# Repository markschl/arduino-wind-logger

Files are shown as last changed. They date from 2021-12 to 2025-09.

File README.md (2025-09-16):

# Data loggers for the ATMOS22 wind sensors (METER)

This repository describes the assembly and operation of low-cost data loggers for the [ATMOS 22 ultrasonic anemometer](https://www.metergroup.com/en/meter-environment/products/atmos-22-ultrasonic-anemometer) (METER group). Two different assemblies of Arduino-compatible components are presented with the programming code needed to operate the loggers in low-power mode. The output files with wind and temperature measurements are saved on a microSD card.

## Logger assembly

Two kinds of logger boards with a microSD card holder were used: [SODAQ Autonomo](https://support.sodaq.com/Boards/Autonomo) (discontinued) and [Adafruit Feather M0 Adalogger](https://learn.adafruit.com/adafruit-feather-m0-adalogger). An [external DS3231 RTC](https://learn.adafruit.com/adafruit-ds3231-precision-rtc-breakout) was connected for timekeeping and waking up the device from sleep mode. A button (switch) was connected to one of the pins and ground to interact with the logger. The pin numbers, to which RTC, button and sensor were connected are defined in `SodaqAutonomo.h` and `FeatherM0.h`.

The boards were powered by a 2700mAh Li-Ion battery, which was charged by a small 0.5 W / 100mA solar panel. The SODAQ Autonomo has an integrated solar power management circuit, while the Feather M0 Adalogger was powered by a separate [solar power manager](https://wiki.dfrobot.com/Solar_Power_Manager_5V_SKU__DFR0559) (DFROBOT DFR0559) providing a 5V power source and connected by USB, simultaneously providing power to the ATMOS22 sensor, which requires of minimum 3.6 V. For the SODAQ Autonomo wit an operating voltage of 3.3V, an additional [DC/DC boost converter](https://learn.adafruit.com/adafruit-powerboost) was needed to provide a 5V source. The solar chargers seem not to adapt to cold (< 0 °C) temperatures and thus may not be ideal for continued operation in winter.

Simple diagrams of the wiring created using the software [Fritzing](https://fritzing.org/download/) are [provided here](circuits).

## How to program the loggers

### Setup

First, install the [Arduino IDE](https://www.arduino.cc/en/software) and start it.

Next, board support has to be installed by clicking on File -> Preferences and pasting the necessary JSON file URLs (separated by comma) into the text field at "Additional Boards Manager URLs". Then go to Tools -> Boards Manager, and intall the following:

- [SODAQ Autonomo](https://support.sodaq.com/getting_started/): `http://downloads.sodaq.net/package_sodaq_samd_index.json`, provides *SODAQ SAMD Boards*
- [Adafruit Adalogger](https://learn.adafruit.com/adafruit-feather-m0-adalogger/setup): `https://adafruit.github.io/arduino-board-index/package_adafruit_index.json`, provides *Adafruit SAMD Boards*

#### Ubuntu Linux

For Ubuntu, access to the serial port has to be granted by typing this in the terminal: `sudo adduser $USER dialout`. Then log out and in again.

### Arduino libraries

A few libraries are needed (Tools -> Library Manager):

- *SdFat* by Bill Greimann (tested with versions 2.3.0)
- *RTClib* by Adafruit (2.1.4)
- *Arduino Low Power* by Arduino LLC (1.2.2)
- [*SDI-12*](https://github.com/EnviroDIY/Arduino-SDI-12) by Kevin Smith et al. (2.3.0)

### Preparation

- Open `datalogger/datalogger.ino` in the Arduino IDE. Select the correct board at *Tools -> Boards -> \<board name\>*. There are separate header files named after the boards, which include all the pin settings. If you have a different board or pin wiring, you need to adjust the code and add your own header file with the correct settings.
- **Configuration:** Adjust the variables in "User settings" section if necessary
- At a minimum, give your sensor/logger combo an unique name by setting the **LOGGER_ID**. This name is prepended to all output files and helps to avoid confusion when copying them all to your computer
- Make sure that `DEBUG` is `false` if uploading the final program for autonomous operation (the default is `DEBUG true`, which is useful for setting things up)

#### Configuration

The logger is configured to do *instantaneous measurements every 10 seconds* using the `R4!` command (see [Integrator Guide](http://publications.metergroup.com/Integrator%20Guide/18195%20ATMOS%2022%20Integrator%20Guide.pdf)). The measurement interval can easily be changed in the *User Settings* section. Switching to averaged / maximum values (`R3!` command) requires replacing `sensor.measureR4(logLine)` with `sensor.measureR3(logLine)` in `datalogger.ino`. Other commands will have to be implemented first (in `Sensor.h` / `Sensor.cpp`).

### Uploading the program to the logger

Connect the logger board to the computer using a mini-USB cable. For the the boards to be ready under Ubuntu 20.04, it was usually reqired to double tap the reset button. Make sure that the device is present under *Tools -> Port*, otherwise double tap the reset button another time. `Ctrl + U` will upload the program.

If `DEBUG` is set to `true` (the default) before the upload, the progress of the logger operation can be monitored in the serial console (Tools -> Serial Monitor) while still connected by the USB cable. This mode also allows setting the time of the RTC and formatting the SD card if necessary. For regular operation, the program should again be uploaded with DEBUG disabled.

## Preparing the SD cards

We used SD cards with 2 GB capacity (which is more than enough for long logging). Smaller cards tend to have less powerful chips that [also draw less power](https://thecavepearlproject.org/2015/11/05/a-diy-arduino-data-logger-build-instructions-part-4-power-optimization). Cards smaller than 2GB should be formatted to FAT16. In Linux, this can be done as follows (given the device of the SD card):

```sh
sudo mkdosfs -F 16 /dev/sdb1
```

Alternatively, the logger is able to detect problematic formatting and format the SD card when in debug mode (see above).

## Logger operation

Make sure to upload the program with `DEBUG` set to `false`.

- Startup is indicated by the LED blinking 10x. The SD card must be present. The LED will also light up during wind measurement (which takes a bit less than a second).

- Errors are indicated by the LED blinking 3-5 times every 10 seconds. 3x indicates an error with the SD card (not inserted, wrong format or any writing error). 4x indicates an error with the sensor (not connected, ...). 5x indicates a problem with the clock (RTC). To restart the logger, press the control button or board reset button.

- Before removing the SD card, press the control button (not the reset button) once and wait until the LED light has disappeared. The logger will continue measuring, but blinking twice (long-short) to indicate "detached" logging. After re-inserting the SD card (or a new one), again press the control button. Further regular measurements will be indicated by the "normal" single blinking event of the LED. If the long-short blinking pattern persists, this means that the logger is still in detached mode because there was a problem with the SD card (not inserted / wrong format).

- Every time the SD card is (re-)inserted, the logger creates a new file in the `atmos22` directory named according to the insertion date. The `txt` files can later be combined in Excel or R.

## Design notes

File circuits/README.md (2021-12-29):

# Wiring diagrams

## SODAQ Autonomo

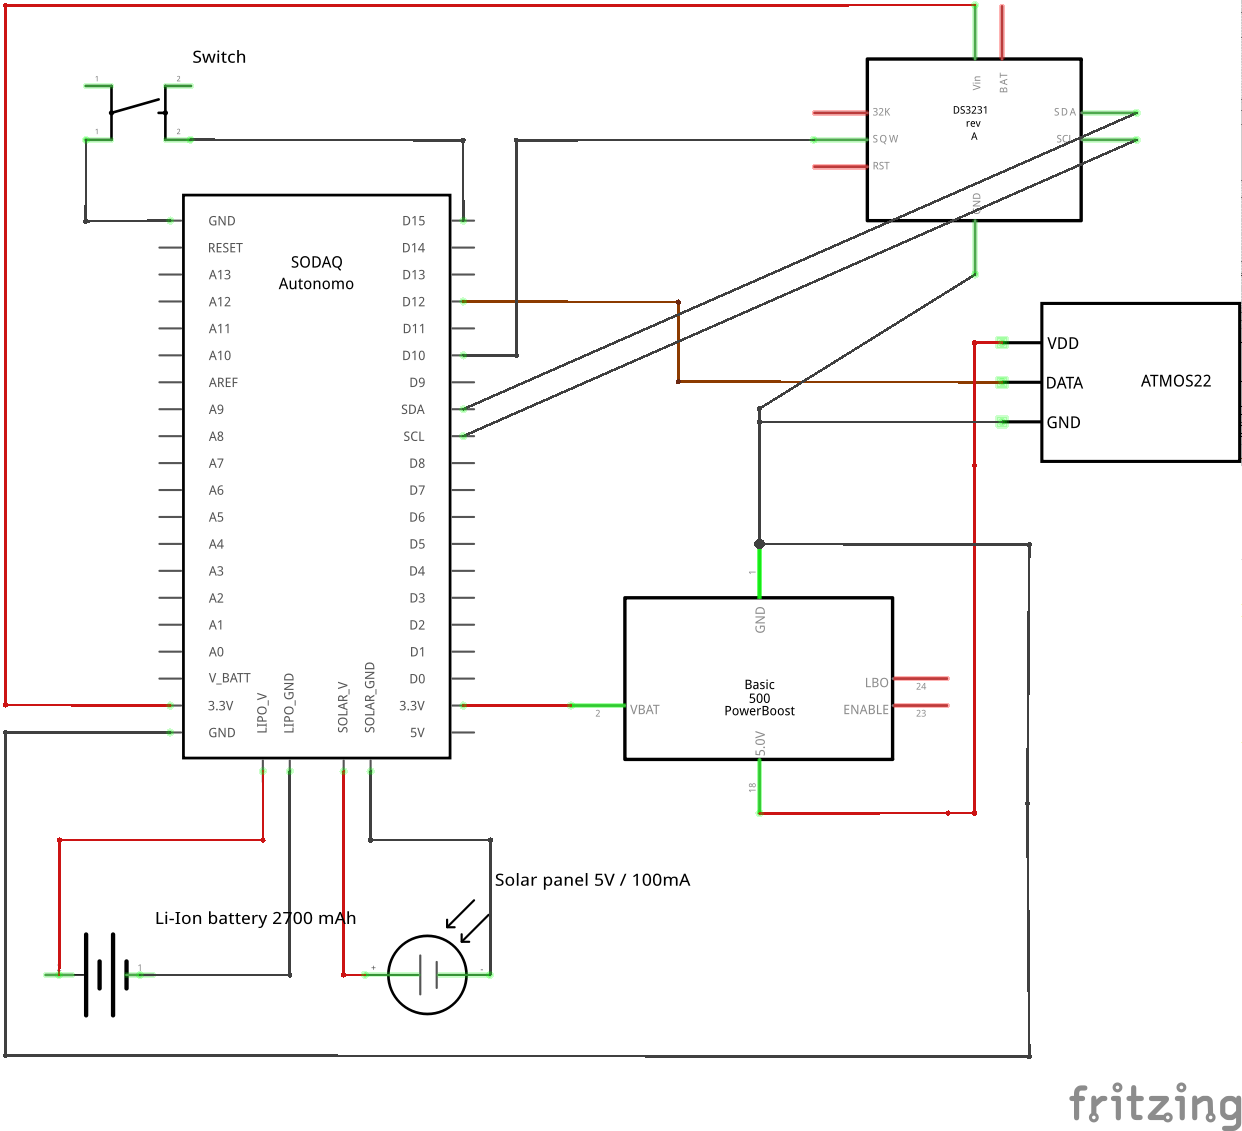
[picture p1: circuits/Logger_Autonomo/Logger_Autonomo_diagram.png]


## Adafruit Feather M0 Adalogger

The diagram does not include the [solar power manager](https://wiki.dfrobot.com/Solar_Power_Manager_5V_SKU__DFR0559) (DFROBOT DFR0559) providing the 5V USB power source.

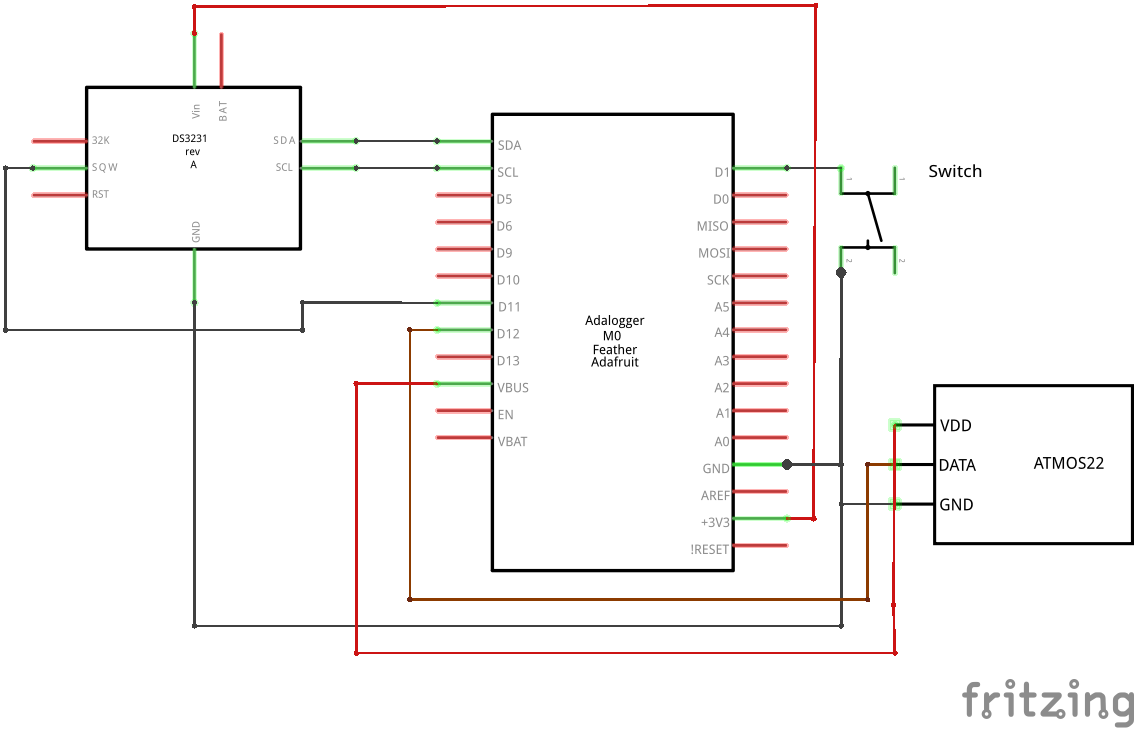
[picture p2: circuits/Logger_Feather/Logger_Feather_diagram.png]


## Fritzing files

The Fritzing parts for the solar panel and SODAQ Autonomo were [obtained here](https://github.com/GabrielNotman/SODAQ_Fritzing) and further modified. The Adafruit parts were [obtained from this page](https://github.com/adafruit/Fritzing-Library). The Li-Ion battery was modified from a battery part from the Fritzing core library. License: CC BY-SA 3.0.

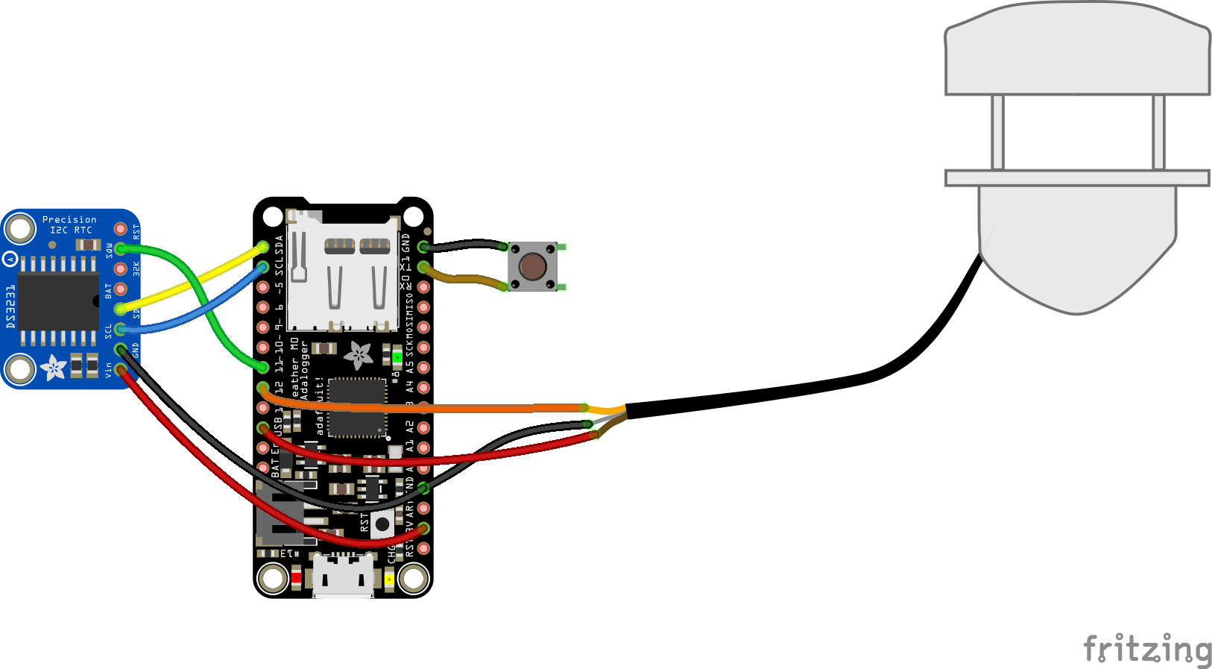
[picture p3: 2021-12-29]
circuits/Logger_Feather/Logger_Feather.png

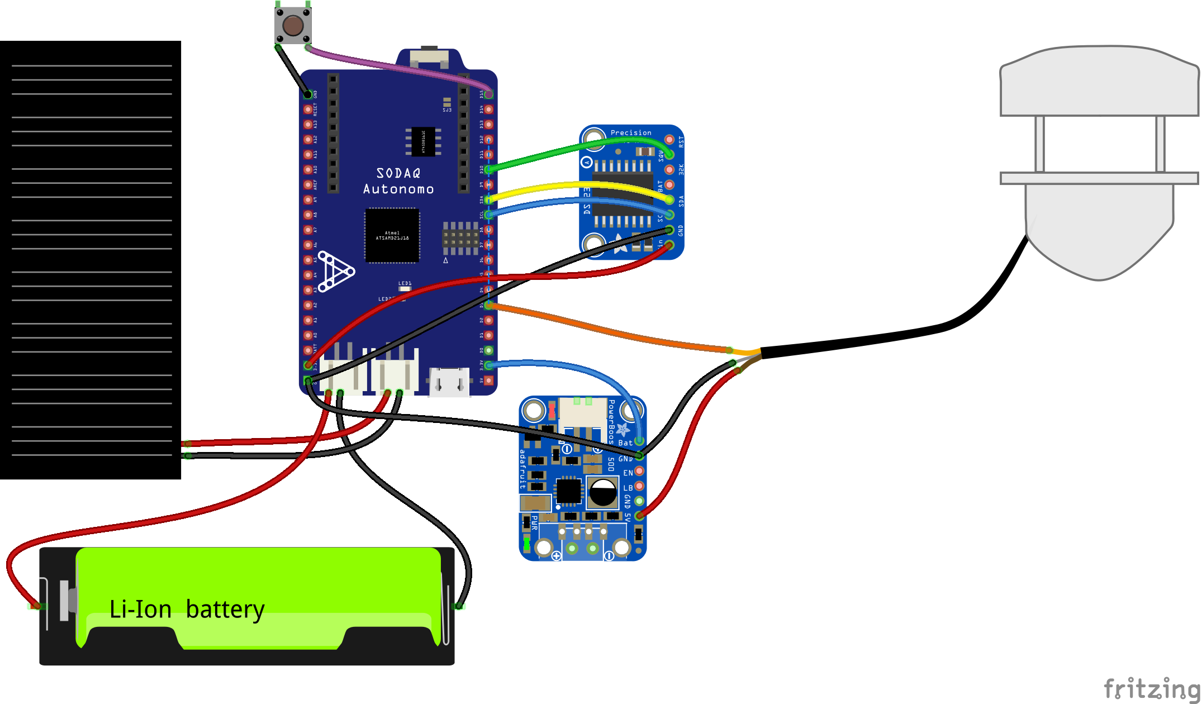
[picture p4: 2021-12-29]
circuits/Logger_Autonomo/Logger_Autonomo.png

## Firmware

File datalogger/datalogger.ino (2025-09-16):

// include libraries
#include "Arduino.h"
#include "RTClib.h"
#include "SDI12.h"
#include "SdFat.h"

// Different boards have different names for the USB serial
#define Serial SERIAL_PORT_MONITOR

// include our own header files
#include "SdLogger.h"
#include "Sensor.h"
#include "system.h"

// --------------------------------------------
// 1. Choose the right board
// --------------------------------------------
// You need to install board support:
// - Sodaq Autonomo: https://support.sodaq.com/getting_started/
// - Adafruit Feather M0: https://learn.adafruit.com/adafruit-feather-m0-adalogger/setup
// Then choose the board that you connected with USB
// - Tools -> Board -> Sodaq Autonomo
// OR
// - Tools -> Board -> Adafruit Feather M0
// Further settings (pin numbers, etc.) are found in header files named after the board,
// which are automatically included (see below)

// --------------------------------------------
// 2. User settings
// --------------------------------------------

// Name of the logger, will be prepended to output file names on the SD card
// NOTE: it is adivable to give your sensor (with its attached logger) an unique
//   name to avoid confusion after copying the files to your computer!!!
#define LOGGER_ID "sensor_1"

// Debug mode: activate with true or 1, deactivate with false or 0
// Used for:
// - debugging (device activity logged to the serial console)
// - adjusting the RTC date and time
// - formatting the SD card with FAT16
// NOTE: the logger will only work autonomously (not attached to computer)
//    setting DEBUG to false
#define DEBUG true

// Name of the output directory
#define BASE_DIR "atmos22"

// Defines how many bytes should be logged to RAM before
// writing to the SD card. Higher numbers will lead to lower
// energy consumption (less frequent writes to SD card),
// but in case of power loss, more data will be lost. 
// Also make sure that there is enough RAM. Memory is reported
// in debug mode.
#define BUFFER_SIZE 16384

// Measurement interval, at least 10s if using the R4! command
// according to ATMOS22 integrator guide
#define MEASUREMENT_INTERVAL_SECONDS 10

// header added on top of every file
#define HEADER \
"date_time\tnorth_speed\teast_speed\tgust_speed\ttemperature\t\
x_orientation\ty_orientation\tbattery_voltage\tboard_temperature\n"

// Error codes (error LED will blink this many times)
#define SD_ERROR 3
#define SENSOR_ERROR 4
#define CLOCK_ERROR 5
// interval, at which erros are indicated
#define ERROR_INTERVAL_SECS 10

// SD settings
#define ENABLE_DEDICATED_SPI 1
#define SDFAT_FILE_TYPE 1

// The baud rate for the output serial port
#define SERIAL_BAUD 9600

// --------------------------------------------
// 3. Set up board and debugging
// --------------------------------------------

#if defined(ARDUINO_SODAQ_AUTONOMO)
  #include "SodaqAutonomo.h"
#elif defined(ADAFRUIT_FEATHER_M0)
  #include "FeatherM0.h"  
#else
  #error Unsupported board
#endif

#ifndef LOGGER_ID
#error "LOGGER_ID not defined"
#endif

// debugging macros
#if DEBUG

bool debugMode = true;
#define PRINT(...) Serial.print(__VA_ARGS__)
#define PRINTLN(...) Serial.println(__VA_ARGS__)
#else

bool debugMode = false;
#define PRINT(...)
#define PRINTLN(...)

#endif

// --------------------------------------------
// 4. Global variables (occupy RAM from the beginning)
// --------------------------------------------

// RTC, SD card, logger, sensor
RTC_DS3231 rtc;
SdFat sd;
SdLogger logger = SdLogger(sd, rtc, LOGGER_ID, BUFFER_SIZE);
Sensor sensor = Sensor(SDI12_PIN);

// Next wake-up time, always incremented by wakeInterval
uint32_t wakeTime = 0;

// Measurement or error reporting interval
uint32_t wakeInterval = MEASUREMENT_INTERVAL_SECONDS;

// The current state of the logger
enum state {
  starting,
  logging,
  detaching,
  detached_logging,
  attaching,
  error,
};

volatile state runState = starting;

// must be true for logging to happen (usually set in ISR)
volatile bool regularWakeup = false;

// SD state
enum sdState { present, inserted, missing, unknown };

#ifdef SD_CARD_DETECT_PIN
// SD card is always present at the start, otherwise
// there will be an error
volatile sdState sdPresence = inserted;
#else
volatile sdState sdPresence = unknown;
#endif

// Buffers for time stamp and logger output
char TimeStamp[] = "0000-00-00T00:00:00Z";
String logLine = "";

// Error code
uint8_t errorNo = 0;

// --------------------------------------------
// 5. Utilities
// --------------------------------------------

void updateTimeStamp(DateTime t) {
  // write timestamp in ISO 8601 (https://en.wikipedia.org/wiki/ISO_8601)
  sprintf(TimeStamp, "%d-%02d-%02dT%02d:%02d:%02dZ", t.year(), t.month(),
          t.day(), t.hour(), t.minute(), t.second());
}

void setError(uint8_t no) {
  errorNo = no;
  runState = error;
  wakeInterval = ERROR_INTERVAL_SECS;
}

// blink internal LED(s)
void blink(uint8_t pin, uint8_t pin2, uint32_t n, uint32_t wait_ms) {
  for (uint32_t i = 0; i < n; i++) {
    digitalWrite(pin, HIGH);
    if (pin2 != NULL) {
      digitalWrite(pin2, HIGH);
    }
    delay(wait_ms);
    digitalWrite(pin, LOW);
    if (pin2 != NULL) {
      digitalWrite(pin2, LOW);
    }
    delay(wait_ms);
  }
}

void sdDateTimeCallback(uint16_t* date, uint16_t* time) {
  DateTime now = rtc.now();
  *date = FAT_DATE(now.year(), now.month(), now.day());
  *time = FAT_TIME(now.hour(), now.minute(), now.second());
}

// prompt for yes / no answer
bool getAnswer(bool defaultYes) {
  Serial.setTimeout(100);
  while (true) {
    while (!Serial.available())
      ;
    String answer = Serial.readString();
    if (answer.length() >= 2 && answer[1] == '\r' || answer[1] == '\n') {
      switch (answer[0]) {
        case 'y':
        case 'Y':
          return true;
        case '\n':
        case '\r':
          return defaultYes;
        case 'n':
        case 'N':
          return false;
      }
    }
    Serial.println(F("Unknown answer."));
  }
}

// --------------------------------------------
// 6. Setup code
// --------------------------------------------

void setup() {
#if DEBUG
  Serial.begin(9600);
  while (!Serial)
    ;
#endif

  // LEDs (light on during setup)
  pinMode(LED_PIN, OUTPUT);
  pinMode(ERROR_LED_PIN, OUTPUT);
  digitalWrite(LED_PIN, HIGH);

  PRINTLN(F("Setting up the external RTC clock..."));
  if (!setupClock()) {
    // loop() will not work, since it depends on the RTC
    // waking up the device periodically. Therefore, we just
    // return, leaving the LED on.
    return;
  }
  // Set this when resetting after error
  wakeInterval = MEASUREMENT_INTERVAL_SECONDS;
  // Set the initial wake time as soon as possible,
  // (just after the reset button was pressed).
  // The first loop call will assume it was woken up at this time.
  wakeTime = rtc.now().unixtime();
  pinMode(RTC_INTERRUPT_PIN, INPUT_PULLUP);
  // Configure clock interrupt on the falling edge from the SQW pin
  // Some additional internal settings are needed for SAMD21 to wake up on
  // external RTC interrupts, which is done by LowPower.
  LowPower.attachInterruptWakeup(digitalPinToInterrupt(RTC_INTERRUPT_PIN),
                                 rtcISR, FALLING);

  PRINTLN(F("Setting up the sensor..."));
  sensor.init();
  if (!sensor.isConnected()) {
    PRINTLN(F("Sensor not found at default address"));
    setError(SENSOR_ERROR);
  }

  PRINTLN(F("Setting up the SD logger..."));
  if (!setupSD()) {
    setError(SD_ERROR);
  }
  logger.setBaseDir(BASE_DIR);
  logger.setHeader(HEADER);
  logLine.reserve(100);

  // // Make sure the internal LED is off
  digitalWrite(LED_BUILTIN, LOW);
  PRINTLN(F("... setup done."));
}

bool setupClock() {
  if (!rtc.begin()) {
    PRINTLN(F("Couldn't find RTC"));
    return false;
  }

  // Initial actions according to
  // https://github.com/adafruit/RTClib/blob/master/examples/DS3231_alarm/DS3231_alarm.ino
  rtc.disable32K();
  rtc.clearAlarm(1);
  rtc.clearAlarm(2);
  rtc.writeSqwPinMode(DS3231_OFF);
  rtc.disableAlarm(2);

#if DEBUG
  while (Serial.read() != -1);
  updateTimeStamp(rtc.now());
  Serial.print(F("Time is: "));
  Serial.print(TimeStamp);
  Serial.println(F(". Do you want to set the clock (y/n)? [default: n]"));
  if (getAnswer(false)) {
    syncClock();
  }
#endif
  return true;
}

void syncClock() {
  while (true) {
    Serial.println(
        F("Please close the serial monitor and type the following:\r\ndate +%s "
          "> /dev/ttyACM0"));
    Serial.println(
        F("in the terminal (Unix). Then re-open the serial monitor."));
    // based on
    // https://forum.arduino.cc/index.php?topic=367987.msg2536880#msg2536880
    while (!Serial.available());
    // read timestamp and set time immediately
    unsigned long pctime = Serial.parseInt();
    if (pctime != 0) {
      // Sync Arduino clock to the time received on the serial port
      rtc.adjust(DateTime(pctime));
    }
    // Disable Serial in order to block until the window is re-opened
    Serial.end();
    while (!Serial);
    Serial.begin(SERIAL_BAUD);
    Serial.println(pctime);
    if (pctime == 0) {
      Serial.println(F("No valid number was received, repeating."));
    } else {
      Serial.print(F("It worked, time is now: "));
      updateTimeStamp(rtc.now());
      Serial.println(TimeStamp);
      break;
    }
  }
}

bool setupSD() {
  while (true) {
    uint8_t res = initSD();
    if (res != 0) {
#if DEBUG
      if (res == 1) {
        Serial.println(F("Should the card be reformatted? (y/n) [default: n]"));
        if (getAnswer(false)) {
          Serial.println(
              F("All data will be erased, are you sure? (y/n) [default: n]"));
          if (getAnswer(false)) {
            if (!formatCard()) {
              return false;
            }
            // again initialize card and show
            continue;
          }
        }
      }
#endif
      return false;
    }
    break;
  }

// enable card detection (if feature present)
#ifdef SD_CARD_DETECT_PIN
  pinMode(SD_CARD_DETECT_PIN, INPUT_PULLUP);
  attachInterrupt(digitalPinToInterrupt(SD_CARD_DETECT_PIN), sdChange, CHANGE);
#endif

  // Button: attach interrupts
  pinMode(BUTTON_PIN, INPUT_PULLUP);
  attachInterrupt(digitalPinToInterrupt(BUTTON_PIN), button_change, FALLING);

  // make sure the files have the correct creation date / time
  // according to https://forum.arduino.cc/index.php?topic=348562.0
  SdFile::dateTimeCallback(sdDateTimeCallback);
  return true;
}

uint8_t initSD() {
  // Initialize properly, see:
  // https://github.com/greiman/SdFat/blob/master/examples/QuickStart/QuickStart.ino
  if (!sd.begin(SDCARD_PIN)) {
    PRINTLN(F("Card initialization failed!"));
    if (sd.card()->errorCode()) {
      PRINT(F("Card not inserted? Error code: "));
      PRINT(sd.card()->errorCode());
      PRINT(F("Data: "));
      PRINTLN(sd.card()->errorData());
      return 2;
    } else if (sd.vol()->fatType() == 0) {
      PRINTLN(F("Can't find a valid FAT16/FAT32 partition."));
      return 1;
    } else {
      PRINTLN(F("Reason unknown."));
      return 1;
    }
  }

  uint32_t size = sd.card()->sectorCount();
  if (size == 0) {
    PRINTLN(F("Can't determine the card size."));
    PRINTLN(F("Try another SD card or reduce the SPI bus speed"));
    return 2;
  }

  uint32_t sizeMB = 0.000512 * size + 0.5;
  PRINT(F("  Card size: "));
  PRINT(sizeMB);
  PRINTLN(F(" MB"));
  PRINT(F("  Volume type: FAT"));
  PRINTLN(sd.vol()->fatType());
  PRINT(F("  Cluster size: "));
  PRINT(sd.vol()->bytesPerCluster() / 1024.);
  PRINTLN(F(" KiB"));

  if ((sizeMB > 1100 && sd.vol()->sectorsPerCluster() < 64) ||
      (sizeMB < 2200 && sd.vol()->fatType() == 32)) {
    PRINTLN(F("Reformat card using cluster size of 32 KB for cards > 1 GB."));
    PRINTLN(F("Only cards larger than 2 GB should be formatted FAT32."));
    return 1;
  }
  return 0;
}
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

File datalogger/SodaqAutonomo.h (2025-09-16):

// Autonomo
#define RTC_INTERRUPT_PIN 10       // Pin for RTC interrupt
#define BUTTON_PIN 15              // Pin for the control button
#define SDCARD_PIN CS_SD           // Pin for communicating with the SD reader (chip select / CS pin)
#define LED_PIN LED_BUILTIN        // Pin of a diagnostic LED
#define ERROR_LED_PIN LED_BUILTIN  // Pin of LED used for emitting error codes
#define SDI12_PIN 3                // Pin of the SDI-12 data bus


//These constants are used for reading the battery voltage
#define ADC_AREF 3.3
#define BATVOLTPIN BAT_VOLT
#define BATVOLT_R1 4.7
#define BATVOLT_R2 10

// Function for getting battery voltage in mV
float GetBatteryVoltageMV() {
  uint16_t batteryVoltage = analogRead(BATVOLTPIN);
  return (ADC_AREF / 1.023) * (BATVOLT_R1 + BATVOLT_R2) / BATVOLT_R2 * batteryVoltage;
}

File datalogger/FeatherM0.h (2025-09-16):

// --------------------------------------------
// 2. Pins
// --------------------------------------------

//// Adalogger M0
#define RTC_INTERRUPT_PIN 11  // Pin for RTC interrupt
#define BUTTON_PIN 1          // Pin for the control button
#define SDCARD_PIN 4          // Pin for communicating with the SD reader (chip select / CS pin)
#define SD_CARD_DETECT_PIN 7  // (optional): Pin signalling if the SD card was inserted/removed
#define LED_PIN 8             // Pin of a diagnostic LED
#define ERROR_LED_PIN 13      // Pin of LED used for emitting error codes
#define SDI12_PIN 12          // Pin of the SDI-12 data bus

// Function for getting battery voltage in mV
float GetBatteryVoltageMV() {
  // not known on this board as the power management is done separately
  return 0.;
}
